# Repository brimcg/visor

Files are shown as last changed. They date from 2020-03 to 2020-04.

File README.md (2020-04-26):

# Protective Face Shield for COVID-19

## Design for Reusable Headband with Low Cost Replacement Shields

> *Brand new design released 4/7/2020*
>  - *Added design for 3DVerkstan North American shields 4/8/2020*
>  - *Added design for Prusa shields 4/10/2020*
>
> ### Introducing *H2*!
>
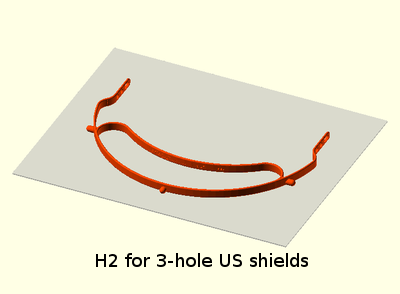
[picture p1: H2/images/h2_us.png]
H2
> 
>
> This ground-up new design takes full advantage of the innovations in our slim cord design and features:
> - 30% reduced print time and material compared to the last slim design.  That's a time and material reduction of *3.5X* compared to the Prusa RC2.
> - Smooth integrated shield and arm design.  Reduces breakage points and hard edges.  Much easier to clean without excessive tight spaces!
> - Flexible brow band design to provide comfort while using widely available fixed length cords.
> - Integrated cinch holes for cord length adjustment.
>
> - You can download STL models in the Makers section now!  Keep in tune to see our upcoming laser cut version H2L.

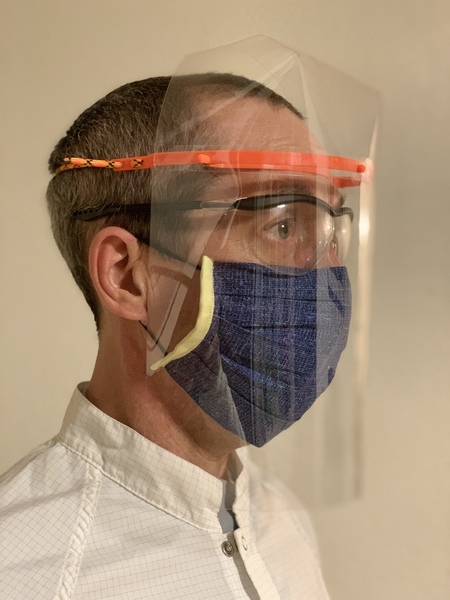
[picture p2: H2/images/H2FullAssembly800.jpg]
full assembled model


Fully assembled H2 headband with face shield and brow shield

---

The urgent need for personal protection equipment in this time of covid19 pandemic is the motivation for these documents.  This is an attempt to provide additional equipment by local community members to help with any shortages of approved equipment.  Please feel free to submit your own suggestions and feedback.

---
---

### For Users

Visors to shield the face are the first line of defense when confronted with infected persons.  They can be up to [92-96% effective](https://www.ncbi.nlm.nih.gov/pmc/articles/PMC5015006/#S3title) as reported by NIH.  It is the purpose of these designs to create a reusable headband that supports low cost, easily replacable shields.  You'll find my NIH design submission [here](https://3dprint.nih.gov/discover/3dpx-013642). Cheap plastic shields can consist of transparency sheets, lamination sheets, or other clear plastic sheets.  Or they can be [purchased](https://www.professionalplastics.com/PETGSHEET) in many different bulk forms; Professional Plastics has tabs for full sheets or cut-to-size.  I think I would recommend 0.020 sheet thickness in the full sheet tab to minimize cost.  I am not affiliated with Professional Plastics, nor have I even purchased from them, so take this info as a potential lead.

To make shields easy to obtain in the US market, a standard three-hole punch design is utilized.  Thus high volume production of shields requires only a ream of transparency sheets and a three-hole punch, both of which are widely available.  Alternate shield materials can also be used if dimensioned to the standard 11" width.

Additional shield designs that have gained traction recently are [3DVerkstan](https://3dverkstan.se/protective-visor/protective-visor-versions/) and [Prusa](https://www.prusaprinters.org/prints/25857-prusa-protective-face-shield-rc1).  Depending upon who you are working with, they may have a preferred shield design.  As such, I've provided designs that are compatible with these other shields.  See in the Maker section below.  If you have a shield design with different hole placements that you would like me to support, send a request to the contact listed below. If reasonable, I can publish a supporting design rather quickly.

#### Instructions

- [Threading](LoopThread/ThreadInstructions.md) of band for H2, slim cord and older cinch designs.  Tip:  The band or cord should be approximately 18" (46cm).
- Making shields for [three-hole design](3HoleShieldInstructions.md)
- Making top [brow shields](BrowShieldInstructions.md) for three-hole design
- Don't expose the plastics to high temperature.  The heat will deform the material.

---
---

### For Makers
Introducing our brand new released H2 design.  Created from scratch to fully take advantage of the innovations introduced in the slim cord design, H2 designs the shield band to smoothly flow into the arms with a cord cinch.  The continuous flow improves strength and reduces hard edges.  And most importantly, the new H2 design reduces print time and filament by 30% compared to the prior slim cord design.  That's a 3.5X improvement in print speed compared to the original Prusa RC2 headband!

If you have a shield design with different hole placements that you would like me to support, send a request to the contact listed below. If reasonable, I can publish a supporting design rather quickly. 

#### Most Recent H2 STL Models
I've been printing these models for donation to our local county health department on a Prusa i3 MK3.  I'm using PrusaSlicer 2.2.0 with PETG as material, 0.4mm nozzle, 0.3mm height, 70% infill, no supports, no brim.  The high infill is only a small time penalty and gives a bit more robustness to the joins.  Under these conditions, I'm seeing 1:02 print times for a Qty 2 piece print.

##### H2 STL models for 3-hole shields using US standard hole punch
 - Three-pin **H2** headband with cinch [(Qty 1)](H2/stl/so_h2_us.stl) [(Qty 2)](H2/stl/so_h2_us_qty2.stl) for paracord
 
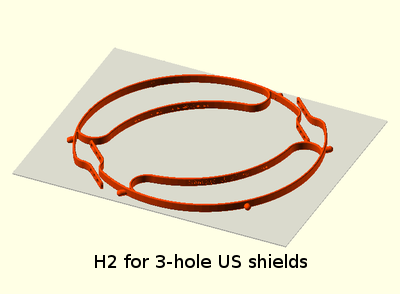
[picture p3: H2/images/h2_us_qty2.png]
H2 Qty 1 print 

##### H2 STL models for 3DVerkstan North American shields
 - Six-pin **H2** headband with cinch [(Qty 1)](H2/stl/so_h2_us_verkstan.stl) [(Qty 2)](H2/stl/so_h2_us_verkstan_qty2.stl) for paracord
 
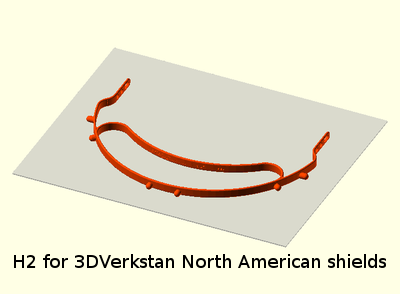
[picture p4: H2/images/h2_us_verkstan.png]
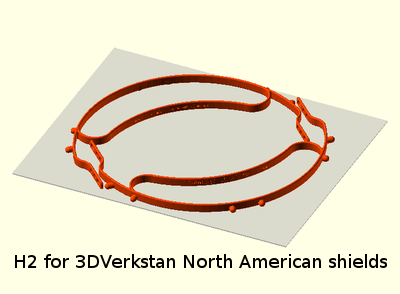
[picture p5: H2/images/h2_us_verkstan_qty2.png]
 

##### H2 STL models for Prusa shields
 - Four-pin **H2** headband with cinch [(Qty 1)](H2/stl/so_h2_prusa.stl) [(Qty 2)](H2/stl/so_h2_prusa_qty2.stl) for paracord
 
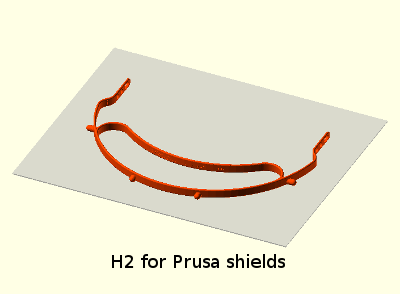
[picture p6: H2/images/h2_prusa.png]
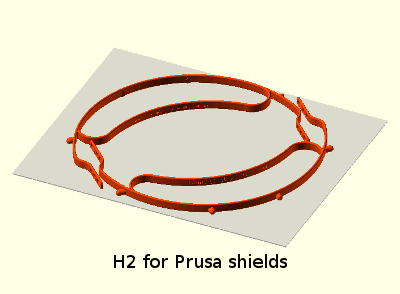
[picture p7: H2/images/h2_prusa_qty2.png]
 

### Archive of older designs

Help generate headbands for our urgent care providers. Choose a design that fits the band that you can obtain, or modify to your own design.  If you do create equipment, it is important to create a sterile environment and handling so that you don't accidentally transmit any virus.  Here you will find:

#### STL models
I've included a number of preconfigured STL models for different configurations (see **Design Tools** below for generating your own variations of STL).  Which model to choose will be determined by the elastic band materials you can obtain.  You can import any of these directly to your slicer (PETG is recommended material, 0.4mm nozzle, 0.2mm height, 20% infill):

##### STL design models for 3-hole shields using US standard hole punch
- Three-pin headband with **slim cord design** [(Qty 1)](older/stl/covid19_headband_3hole_cord_slim.stl) [(Qty 2)](older/stl/covid19_headband_3hole_cord_slim_qty2.stl) for parachute cord strap. Soft spring browband design provides elasticity.  *Slim design reduces print time and material by half!*

- Three-pin headband with **cinch design** [(Qty 1)](older/stl/covid19_headband_3hole_cinch.stl) [(Qty 2)](older/stl/covid19_headband_3hole_cinch_qty2.stl) for flat 3/4" (38mm) elastic bands (non-elastic bands can also marginally work)

- Three-pin headband with **button design** [(Qty 1)](older/stl/covid19_headband_3hole_button.stl) [(Qty 2)](older/stl/covid19_headband_3hole_button_qty2.stl) for button hole elastic band  (Update: Prusa has newly released their official version of this type of design.)

##### STL design models for 4-hole shields based on original Prusa RC2
- Four-pin headband with **slim cord design** [(Qty 1)](older/stl/covid19_headband_rc3_cord_slim.stl) [(Qty 2)](older/stl/covid19_headband_rc3_cord_slim_qty2.stl) for parachute cord strap. Soft spring browband design provides elasticity.  *Slim design reduces print time and material by half!*

- Four-pin headband with **cinch design** [(Qty 1)](older/stl/covid19_headband_rc2_cinch.stl) [(Qty 2)](older/stl/covid19_headband_rc2_cinch_qty2.stl)

- Four-pin unmodified **original Prusa design RC2** [(Qty 1)](older/stl/covid19_headband_rc2_button.stl) [(Qty 2)](older/stl/covid19_headband_rc2_button_qty2.stl) with button design 

##### CAD design tools used here so you can do your own modifications:

- OpenSCAD design [software](https://www.openscad.org/).  You'll need to read their documents if it's new to you.
- OpenSCAD design [code](older/covid19_headband_mods.scad) used to generate modified STL models (except slim cord design or new H2). You can easily choose your type and strap dimensions, self-expanatory parameters at beginning of the code.  Or use the code as a base for you own design code.

---

Thanks Josef Prusa and team for your open design upon which the first visors were based.  Original Prusa RC2 model was obtained [here](https://www.prusaprinters.org/prints/25857-prusa-protective-face-shield-rc1).  Their [link](https://www.prusaprinters.org/prints/25857-prusa-protective-face-shield-rc1) provides good documentation of the design and use.  The modifications here were made to support rapid local use.

---

---

Material has been released under [GPLv3](https://www.gnu.org/licenses/gpl-3.0.html).  Contact me [@brimcg](mailto:brimcg02020@gmail.com)

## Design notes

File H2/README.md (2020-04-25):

# H2 headband for face shield PPE



## Print recommendations
- Material: PETG
- Layer height: 0.3mm
- Infill: 70%
- Support: None
- Brim: Off

- [Gcode](gcode/PrusaMK3/so_h2_us_qty2_0.3mm_PETG_MK3_1h2m.gcode) using recommendations for Qty 2 H2 US 3-pin on a Prusa i3 MK3

## Legend
- US (3-pin for standard US 3-hole punch shields)
- Prusa (4-pin for Prusa shields)
- VerkUS (6-pin for 3DVerdstan V3 US shields)

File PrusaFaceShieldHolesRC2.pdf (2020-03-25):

Transparency Face Shield

Punch 4 holes where indicated

Print with this template 100% scaling Do not “Print to Fit Page”

All design materials open source Visit https://github.com/brimcg/visor

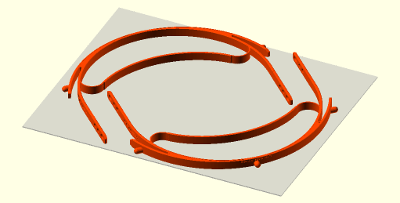
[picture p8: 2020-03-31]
covid19_headband_3hole_cord_slim2.png

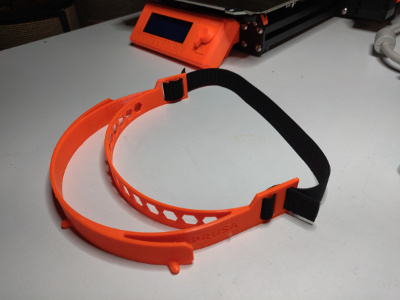
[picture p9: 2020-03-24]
IMG_20200323_084829_small.jpg

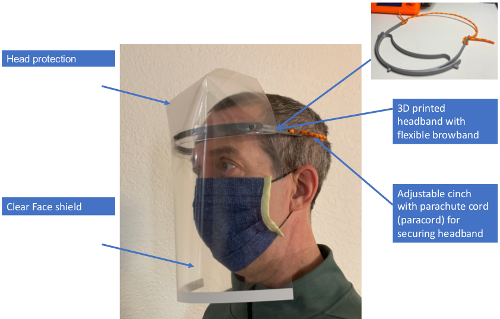
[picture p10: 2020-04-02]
FullFaceHeadShield.png

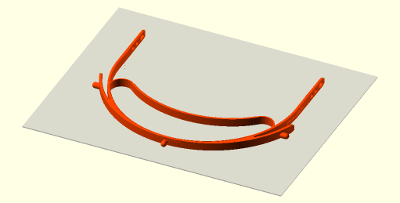
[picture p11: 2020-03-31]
covid19_headband_3hole_cord_slim.png

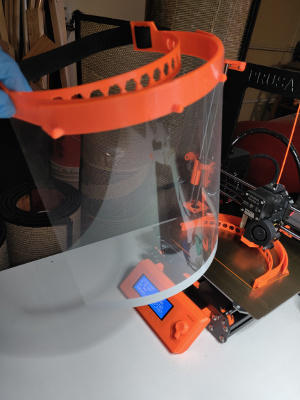
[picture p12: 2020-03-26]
IMG_20200325_170538_small.jpg

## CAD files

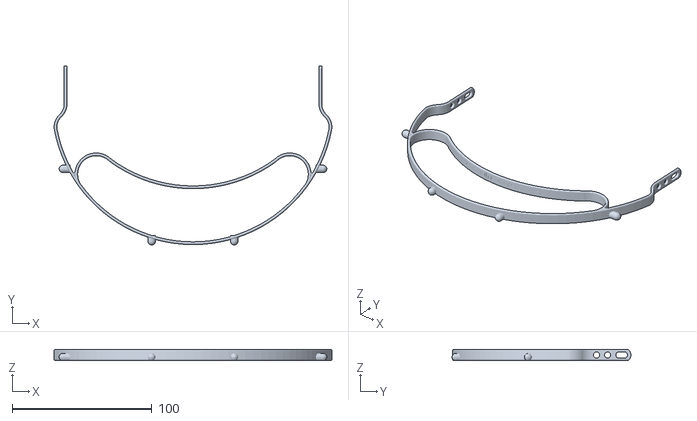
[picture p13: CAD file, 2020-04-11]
H2/stl/so_h2_prusa.stl
198.9 x 128.1 x 7.80

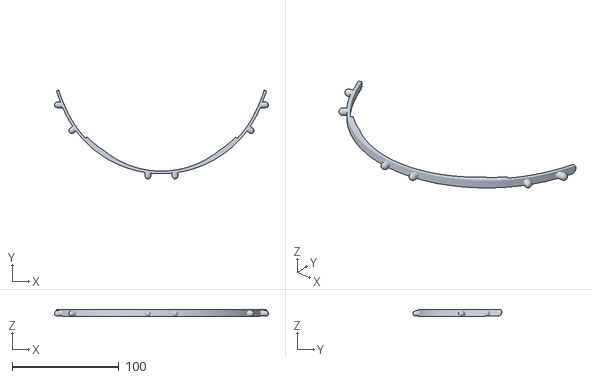
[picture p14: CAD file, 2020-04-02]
stl/columbia/covid19_headband_verkv3_cord_slim_v1_rev1_pintest.stl
200.4 x 83.1 x 6.20

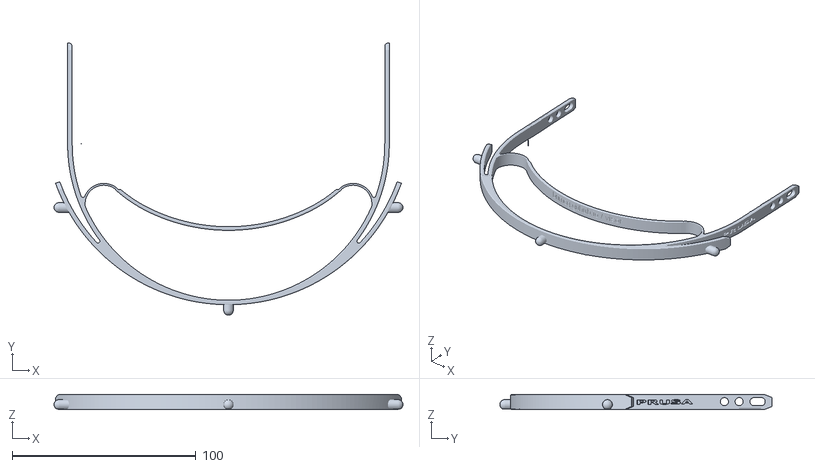
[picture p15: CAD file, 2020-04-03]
stl/covid19_headband_3hole_cord_slim.stl
189.9 x 148.1 x 8.00

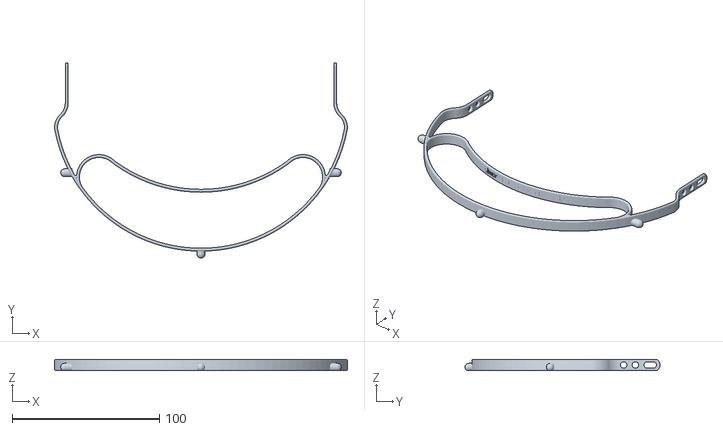
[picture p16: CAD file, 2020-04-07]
H2/stl/so_h2_us.stl
198.9 x 132.5 x 7.80

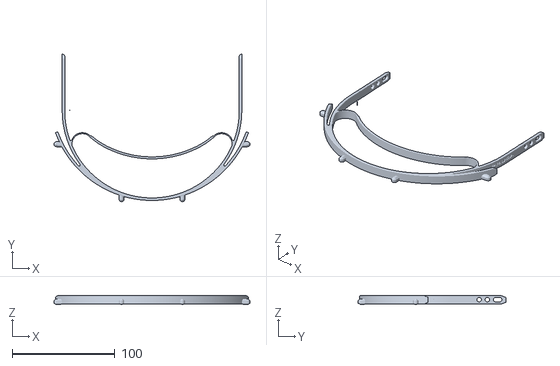
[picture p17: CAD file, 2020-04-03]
stl/covid19_headband_rc3_cord_slim.stl
191.0 x 143.8 x 8.30

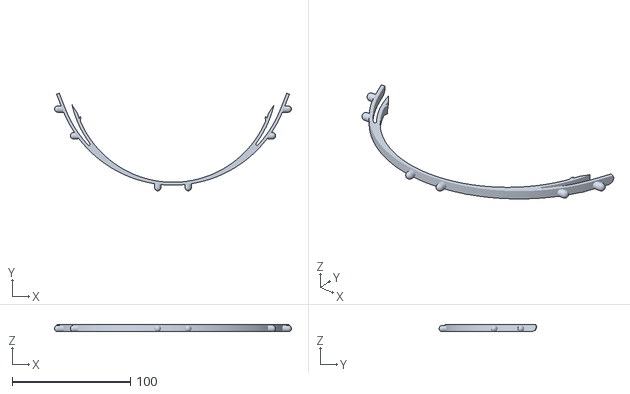
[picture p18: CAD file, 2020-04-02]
stl/columbia/covid19_headband_verkv3_cord_slim_v0_rev0_pintest.stl
200.1 x 82.5 x 6.20

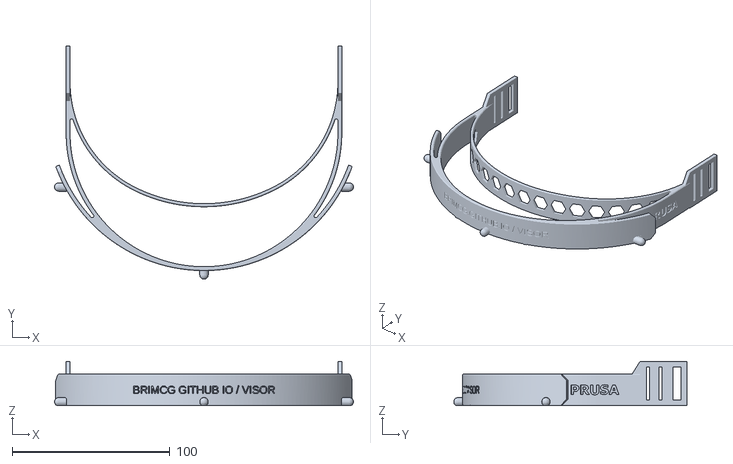
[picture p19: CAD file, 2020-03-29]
stl/covid19_headband_3hole_cinch.stl
189.8 x 148.2 x 28.0

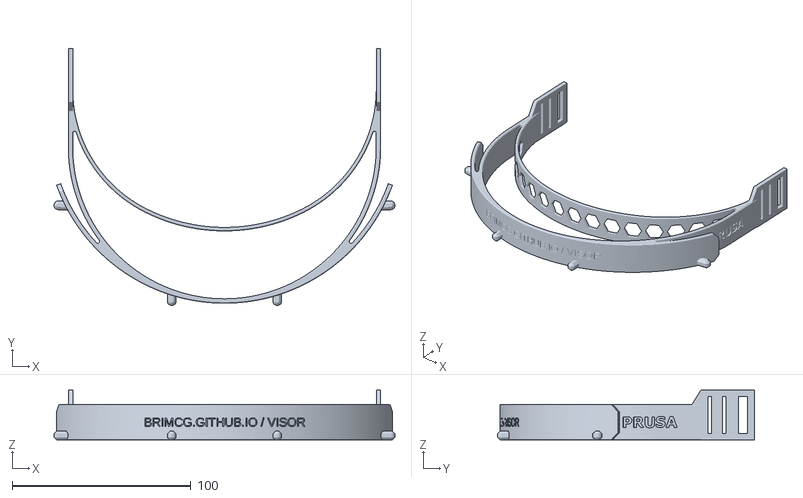
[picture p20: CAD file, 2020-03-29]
stl/covid19_headband_rc2_cinch.stl
191.0 x 144.0 x 28.0

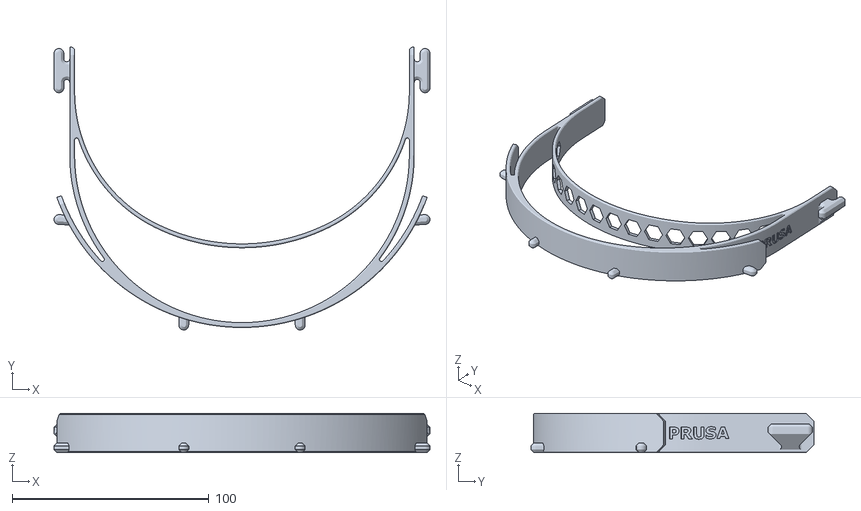
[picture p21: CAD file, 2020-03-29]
stl/covid19_headband_rc2_button.stl
191.0 x 143.8 x 20.0

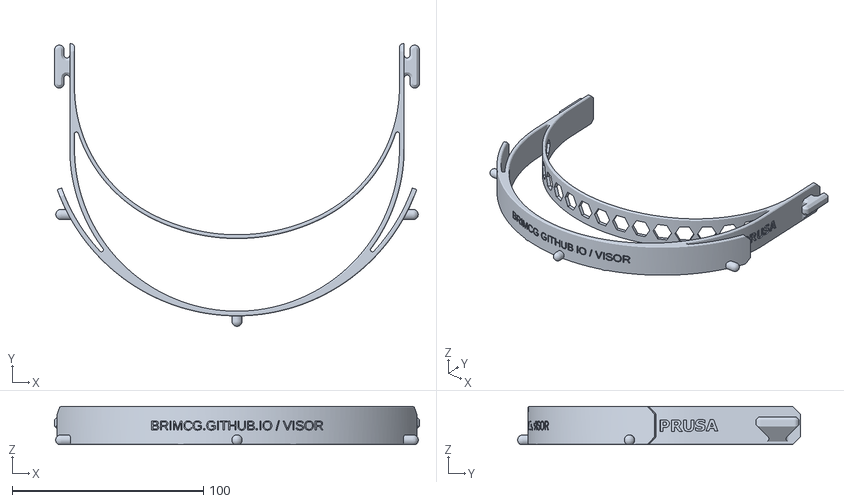
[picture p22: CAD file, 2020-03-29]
stl/covid19_headband_3hole_button.stl
191.0 x 148.0 x 20.0

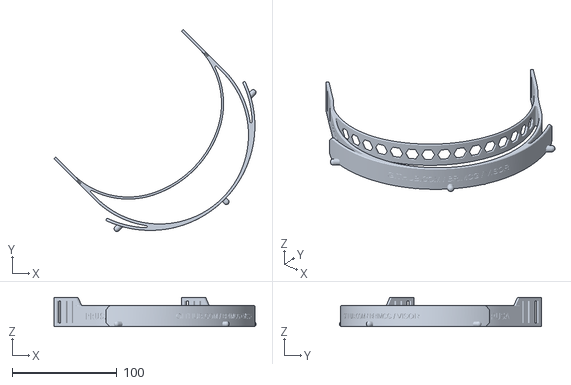
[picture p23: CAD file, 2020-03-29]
stl/covid19_headband_3hole_cinch_qty2.stl
193.1 x 193.1 x 28.0

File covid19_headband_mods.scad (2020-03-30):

////////////////////////////////////////////////
//Prusa headband modifications
//Brian McGinnis 3/26/2020
//Creative Commons Zero v1.0 Universal
////////////////////////////////////////////////

qty = 1;			// >1 will print 2 max

// Design type based off Prusa headband RC2 3/26/2020
// https://www.prusaprinters.org/prints/25857-prusa-protective-face-shield-rc1

3_hole = true;		// false for original Prusa 4-hole RC2
cinch = true;		// false for original Prusa button

pintest = false;	// true to build cropped part for pin location testing to save time and material;

// Design variable for different elastic band dimensions

elastic_width = 20;
elastic_width_margin = 1;
slot_narrow = 2;
slot_wide = 5;
ew = elastic_width + elastic_width_margin;
eh = 3.5;


// Hack design of Prusa headband RC2 and clean off their tabs for button hole elastic and pins for 4-hole, if specified

headband_left = 8;
headband_right = 180.5;
shield_center = [(headband_right+2.5-headband_left)/2 + headband_left, 42.6, 0];
shield_radius = 100.1;



module headband_org() {  // Why is it way off to the right?  Anyway hand force it to left corner.
	translate([-749, 65, 10]) import("covid19_headband_rc2.stl", convexity=4);
//	translate([103.3, 74, 12]) import("covid19_headband_rc3.stl", convexity=4);
}

module headband_hack() {
	intersection() {
		if(3_hole) {
			translate([0, 0, -1])translate(shield_center) cylinder(h=25, r=shield_radius, $fn=200, center=false);
			if(!cinch) translate([-1, -1, -1]) cube([headband_right + 25, 25, 25]);
		}
		if(cinch) difference()
		{
			headband_org();
			translate([-1, -1, -1]) cube([headband_right + 25, 25, 25]);
		}
		else headband_org();
	}
}



// Add my cinch strap design

module prism(l, w, h) {
   translate([l, w, 0]) rotate([0, 0, 180]) polyhedron(
		   points=[[0,0,0], [l,0,0], [l,w,0], [0,w,0], [0,w,h], [l,w,h]],
		   faces=[[0,1,2,3],[5,4,3,2],[0,4,5,1],[0,3,4],[5,2,1]]
		   );
}

module extension(x) {
	h = ew + 2*eh;
	if(h < 20) translate([x, 0, 0]) cube([2.5, 30, 20]);
	else translate([x, 0, 0]) cube([2.5, 30, h]);
	if(h > 20) translate([x, 30, 20]) prism(2.5, 5, h-20);
}

module slot(y) {
	translate([-1, 4, eh]) cube([4, y, ew]);
}

module slots() {
	slot(slot_wide);
	translate([0, 12, 0]) slot(slot_narrow);
	translate([0, 20, 0]) slot(slot_narrow);
}

module bandslot(x) {
	translate([x, 0, 0]) slots();
}

module pin(hp) {
	$fn = 20;
	rp = 2.7;
	intersection() {
		translate([0, 0, rp-0.3]) {
			rotate([-90, 0, 0]) cylinder(h=hp, r=rp);
			translate([0, hp, 0]) sphere(rp);
		}
		translate([-rp, 0, 0]) cube([2*rp, 4*rp, 2*rp]);
	}
}

module cinchtabs() {
	// tabs for cinch
	extension(headband_left);
	extension(headband_right);
}

module pins_3hole() {
	// new pins to match 3 hole punch
	spacing = 108 - 2; // had to readjust
	angle = spacing / 100 * 180 / PI;
	sr = shield_radius + 2.5/2;
	x = sr * sin(angle);
	y = sr * cos(angle)-2.5;
	embed = 1.2;
	
	translate([0, shield_radius-embed, 0]) translate(shield_center) pin(4); // center pin
	translate([-x+embed, y, 0]) translate(shield_center) rotate(90) pin(5); //left pin
	translate([x-embed, y, 0]) translate(shield_center) rotate(-90) pin(5); //right pin
}

module headband_ext() {
	headband_hack();
	if(cinch) cinchtabs();
	if(3_hole) pins_3hole();
}

module logo() {		// add web logo only if it's my modification
	if(3_hole || cinch) difference() {
		translate([0, shield_radius-15, 10]) translate(shield_center) rotate([90, 0, 180]) linear_extrude(height = 20) text("BRIMCG.GITHUB.IO / VISOR", size = 5, halign = "center", valign = "center");
		translate([0, 0, 10]) translate(shield_center) cylinder(h=25, r=shield_radius-0.75, $fn=200, center=true);
	}
}

module headband(angle = 0) {
	center = (headband_right+2.5-headband_left)/2 + headband_left;
	rotate([0, 0, angle]) translate([-center, -center+25, 0]) difference() {
		headband_ext();
		logo();

		if(cinch) {
			bandslot(headband_left);
			bandslot(headband_right);
		}

		if(pintest) {	// crop out majority for pin testing
			translate([0, -20, -1]) translate(shield_center) cylinder(h=50, r=shield_radius, $fn=100, center=false); 
			translate([0, 0, 6]) cube([200, 200, 50]); 
		}
	}
}

// Build it!!!
%translate([0, 0, -0.5]) cube([250, 200, 1], center=true);  //virtual Prusa build bed

if(qty > 1) {
	shiftx = 35;
	shifty = 16;
	translate([shiftx, -shifty, 0]) headband(-135);
	translate([-shiftx, shifty, 0]) headband(45);
}
else headband(180);

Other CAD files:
stl/columbia/covid19_headband_verkv3_cord_slim_v0_rev1_pintest.stl
stl/columbia/covid19_headband_verkv3_cord_slim_v1_rev0_pintest.stl
older/covid19_headband_rc2.stl
older/stl/columbia/covid19_headband_verkv3_cord_slim_v0_rev1_pintest.stl
older/covid19_headband_mods.scad
older/stl/columbia/covid19_headband_verkv3_cord_slim_v1_rev0_pintest.stl

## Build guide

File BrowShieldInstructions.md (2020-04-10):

## Instructions for a cheap brow shield

> New!  Updated brow shield design.  Updated instructions and template coming soon.
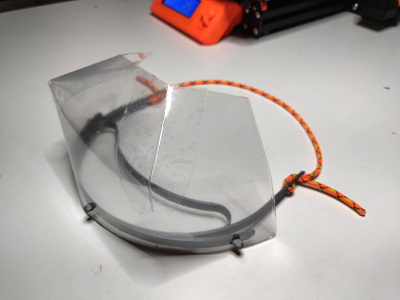
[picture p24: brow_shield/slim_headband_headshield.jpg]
new brow shield
> 

The open top design of the headband allows for flexibility, reduced print time, and reduced material usage.  But it opens up pathway for airborne particles.

To reduce this pathway, here's an idea for a really cheap brow shield.  Requirements:

- 3-hole punch sheet (plastic or paper)
- Scissors or paper cutter
- Stapler or tape

Instructions:

1. Hole punch sheet if not already punched
2. Cut lengthwise to desired height
2. Snap onto headband pins
3. Small fold down center to create crown
4. Staple or tape in place
5. Add transparent face shield!

Photos:

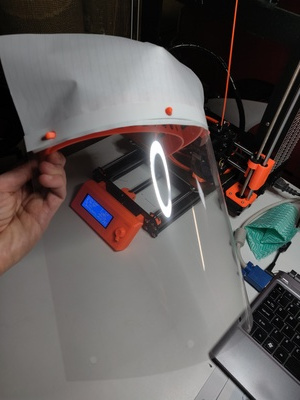
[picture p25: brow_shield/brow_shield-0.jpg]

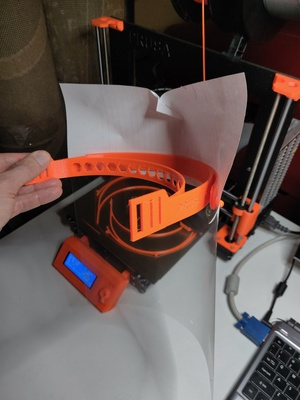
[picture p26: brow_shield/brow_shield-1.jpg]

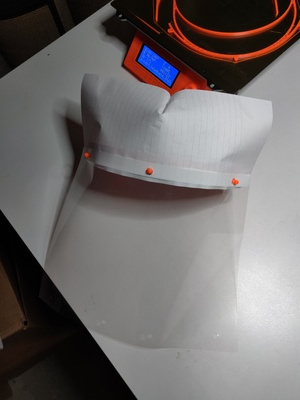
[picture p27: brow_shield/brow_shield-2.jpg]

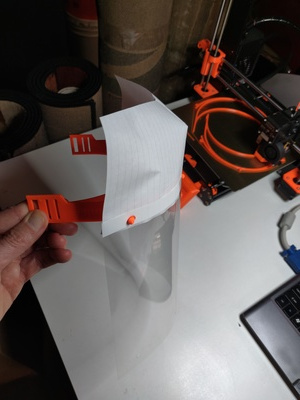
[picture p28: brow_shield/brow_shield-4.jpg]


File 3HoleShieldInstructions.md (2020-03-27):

## Instructions for making three-hole shields

1. Get a standard US three-hole punch
2. Get an 8 1/2" x 11" transparency sheet
3. Punch it along the long side!
4. Slip shield over pins on headband.  Logos face up on headband
5. Next!

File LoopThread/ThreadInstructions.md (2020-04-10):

# How to thread cord for H2 and slim (paracord 550 recommended, easiest method)

Tip: The cord should be approximately 18" (46cm).

Step 1: Thread cord through narrow forwardmost hole from inside of headband

Step 2: Thread cord through narrow center hole from outside of headband

Step 3: Thread cord through wide hole from inside of headband

Step 4: Adjust to length desired and pull tight

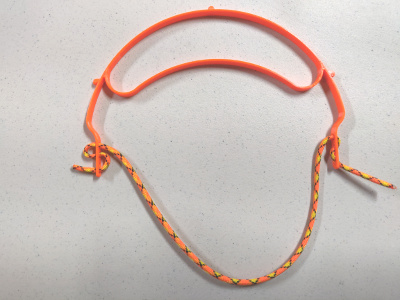
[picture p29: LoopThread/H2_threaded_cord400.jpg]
Cord photo


Repeat on other side!

For wearing adjustment: slip cord in and out in desired direction for a tighter or looser fit.  Adjust for comfortable pressure from the flexible brow band.  To adjust up or down on brow while wearing, lightly push in on both sides of the headband and it will temporarily loosen to ease up/down position.

---

---

# How to thread elastic band (most non-slip method)

Tip: The elastic band should be approximately 18" (46cm).

Step 1: Thread elastic through wide hole from outside of headband

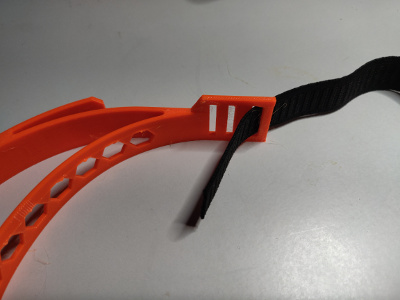
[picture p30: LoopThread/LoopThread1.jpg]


Step 2: Thread elastic through narrow forwardmost hole from inside of headband

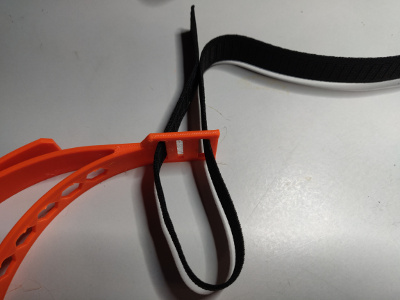
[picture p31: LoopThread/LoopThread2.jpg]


Step 3: Thread elastic through narrow center hole from outside of headband

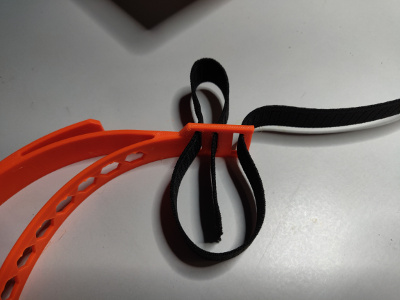
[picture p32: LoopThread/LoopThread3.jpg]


Step 4: Thread elastic through wide hole from inside of headband

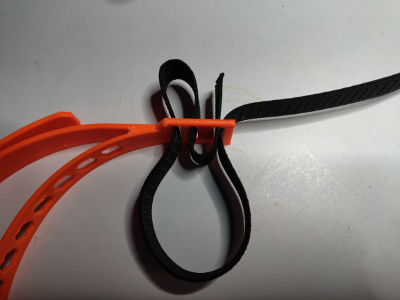
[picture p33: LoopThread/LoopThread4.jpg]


Step 5: Pull tight and adjust to length desired

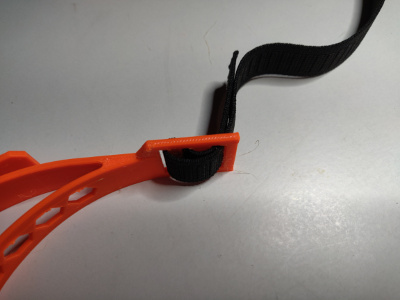
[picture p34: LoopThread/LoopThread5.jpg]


Repeat on other side!

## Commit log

2020-03-24 Photo of modification with strap
2020-03-24 Small photo of modified headband with strap
2020-03-25 Update cut sheet
2020-03-25 Cinch Loop Threading Photos
2020-03-25 Update OpenSCAD code
    [covid19_headband_rc2_bpm03.scad]
2020-03-26 Add assembled visor image
2020-03-27 Major revision
    [covid19_headband_3hole_button.stl, covid19_headband_3hole_cinch.stl, covid19_headband_mods.scad, covid19_headband_rc2.stl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]
2020-03-27 Add three hole shield instructions
2020-03-27 Clean up covid19_headband_mods.scad
    [covid19_headband_mods.scad]
2020-03-28 Update to choose quantity 1 or 2 placed automatically
    [covid19_headband_mods.scad]
2020-03-29 remove stl
    [covid19_headband_3hole_button.stl, covid19_headband_3hole_cinch.stl, covid19_headband_rc2.stl, covid19_headband_rc2_cinch.stl]
2020-03-29 update stl files
    [covid19_headband_3hole_button.stl, covid19_headband_3hole_cinch.stl, covid19_headband_3hole_cinch_qty2.stl, covid19_headband_rc2_button.stl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]
2020-03-30 add slim design
    [covid19_headband_3hole_cord_slim.stl]
2020-03-31 update slim stl
    [covid19_headband_3hole_cord_slim.stl]
2020-03-31 add slim rc3 stl
    [covid19_headband_rc3_cord_slim.stl]
2020-04-02 add columbia stl
    [covid19_headband_verkv3_cord_slim_v0_rev0_pintest.stl, covid19_headband_verkv3_cord_slim_v1_rev0_pintest.stl]
2020-04-02 update stl file location
    [covid19_headband_verkv3_cord_slim_v0_rev0_pintest.stl, covid19_headband_verkv3_cord_slim_v0_rev1_pintest.stl, covid19_headband_verkv3_cord_slim_v1_rev0_pintest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]
2020-04-03 added fillet to browband spring attachment
    [covid19_headband_3hole_cord_slim.stl, covid19_headband_rc3_cord_slim.stl]
2020-04-07 adding H2
    [so_h2_us.stl]
2020-04-08 archive older designs
    [covid19_headband_mods.scad, covid19_headband_rc2.stl]
2020-04-10 add cord threading
2020-04-10 update cord threading
2020-04-11 add stl for prusa shields
    [so_h2_prusa.stl]
2020-04-18 add stacked print gcode
2020-04-18 update stacked print gcode
2020-04-18 added stacked print stl
